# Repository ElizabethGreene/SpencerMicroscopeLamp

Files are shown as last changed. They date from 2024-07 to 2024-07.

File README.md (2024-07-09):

# SpencerMicroscopeLamp
A 3D printable Lamp for an American Optics Spencer Microscope

## Safety warning
This printable is designed for use only with an LED bulb of 3 watts or less.  If a halogen bulb or higher wattage bulb is used, the 3-D printed plastic will melt onto the hot bulb, catch on fire, and cause inestimable damage. Please, I beg you, for the sake of humanity, do not do this.

## Parts required
* 3d printed top and base
* * Recommended Material: Prusament PETG ~ 50 Grams
* * Print at 0.3mm "Draft" settings
* * No support material required
* (2) M3x14mm Socket Head Cap Screws
* * https://amzn.to/3WaNcua
* (2) M3 Nuts
* (4) #4 x 1/2 Wood Screws
* (1) FEIT Electric 25 watt Equivalent G8 Base 120V LED bulb
* * https://amzn.to/4cNXLJ6 (3000k "Warm" Color) or 
* * https://www.homedepot.com/p/Feit-Electric-25-Watt-Equivalent-T4-G8-Bi-Pin-Base-Dimmable-LED-Light-Bulb-in-Daylight-5000K-BP25G8-850-LED-HDRP/319810315 (5000k "Daylight" Color)
* (1) G8 Lamp base
* * https://amzn.to/3XM13Z3 
* (1) Lamp cord with Dimmer
* * https://amzn.to/3XPJfwb
* * NOTE: This is not recommended for new builds. It struggles with low wattage LEDs and causes rolling shutter effects that interfere with photography.  An analog (resistive) dimmer should work better. 
* Solder
* Heatshrink

## Assembly
* 3D print components
* Using M3 screws and nuts, mount lamp base
* Feed Lamp cord through hole in base
* Tie overhand knot in lamp cord as strain relief
* Strip, solder, and heatshrink lamp cord to lamp base wiring
* Tidy wiring so it won't contact bulb using zip tie loop.
* Install bulb
* Secure top cover with 4 #4 wood screws

## Installation
* Using screwdriver, gently spread mirror mount on Microscope to remove mirror.
* Gently spread mirror mount to install new lamp.

## Suggestions for future work
* Test painting or lining interior for less light loss
* Consider Mechanism to allow adjusting bulb position

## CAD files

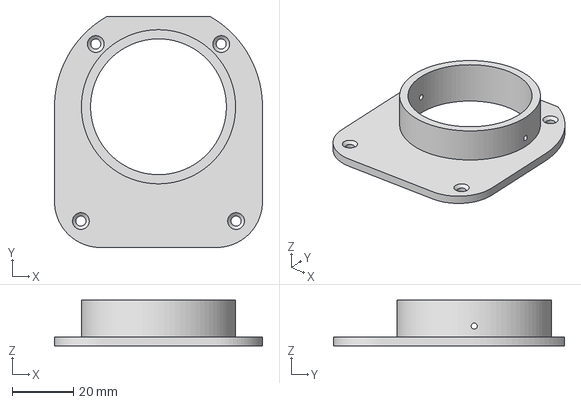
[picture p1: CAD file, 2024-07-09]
Microscope Illuminator Lid.3mf
68.0 x 75.5 x 15.0 mm

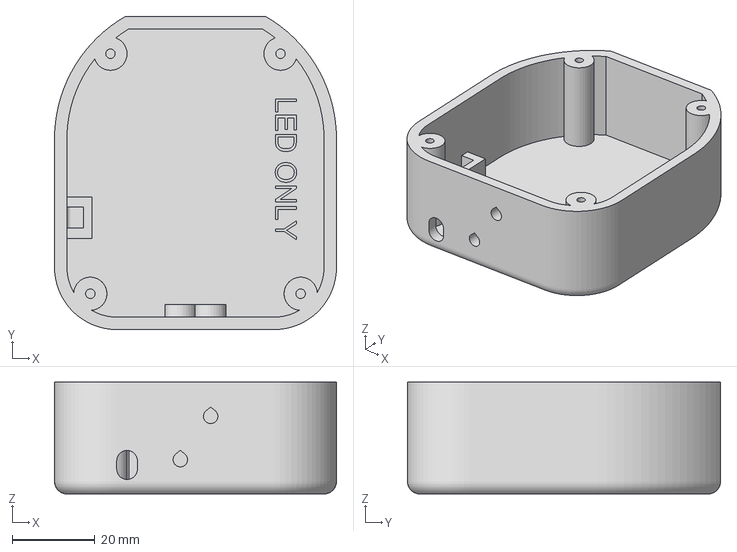
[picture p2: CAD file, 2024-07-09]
Microscope Illuminator Base.3mf
68.0 x 75.5 x 27.0 mm

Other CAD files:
Microscope illuminator.f3d

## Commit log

2024-07-04 V.0.1 Alpha Release Commit
    [Microscope Illuminator Base.3mf, Microscope Illuminator Top.3mf, Microscope illuminator.f3d]
2024-07-04 v1.0.0 fixes
    Moved to semantic version numbers
    Add LED only text to inside of base
    Trimmed 'bulge' to allow closer fitting to stem
    Reduced height slightly
    Increased hole clearances and made 3d printable
    Increased countersink depth on lid
    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
    [Microscope Illuminator Base.3mf, Microscope Illuminator Lid.3mf, Microscope Illuminator Top.3mf, Microscope illuminator.f3d]
2024-07-08 1.0.0 test print 2 updates
    Shortened LED warning, rotated zip-tie loop, increased height of lid ring to allow future addition of filters, diffusers, or gels.
    [Microscope Illuminator Base.3mf, Microscope Illuminator Lid.3mf, Microscope illuminator.f3d]
